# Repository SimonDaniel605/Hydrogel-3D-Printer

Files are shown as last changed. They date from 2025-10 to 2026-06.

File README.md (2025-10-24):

# Hydrogel-3D-Printer

This project aims at the development of a custom hydrogel 3D printer for tissue engineering and research applications for Stellenbosch University. This is a 4th year project for SU's BEng Mechatronics program.

This repository contains the PCB design files, firmware, and supporting documentation for the Hydrogel 3D Printer project.

Name: Simon Craig DANIEL

Student Number: 25848887

Supervisor: Mr. Wayne Swart

Company: Stellenbosch University

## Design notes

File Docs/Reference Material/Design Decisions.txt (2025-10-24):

Based on DESCRIPTION OF PREFERRED FITS (ANSI B4.2): The syrine plunger will use a clearance fit of H9/d10. Therefore the Syringe must have an ID of 20.000-20.052mm and the plunger should have an OD of 19.851-19.935mm. This yields a diametral clearance of 0.065-0.201mm. 

Groove width will be 3.3mm and its diameter will be 16mm (https://ceetak.com/o-ring-calculator/)

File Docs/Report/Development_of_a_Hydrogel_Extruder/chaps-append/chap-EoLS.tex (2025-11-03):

\chapter{Responsible Use of Resources and End-of-Life Strategy }
\section*{Responsible Use of Resources}
The hydrogel bioprinter was developed with the goal of using efficient materials and reusable components. The majority of the mechanical system consists of standard parts, including aluminium extrusions, TR8x8 lead screws, GT2 belts and pulleys, NEMA17 stepper motors, and linear bearings, which can all be reused in future student projects. 6 small PLA parts were 3D printed (4 feet and 2 limit switch mounts), resulting in minimal filament waste. The printer also includes several custom aluminium components (such as the syringe and bed plate) to ensure durability, most of which are made from aluminium plates to minimize machine waste.

The custom PCB was designed to maximise modularity, re-usability, and upgradability, by incorporating 5 stepper ports with breakout driver headers (StepStick form factor), 12 V switching ports, EEPROM storage, USB and SD card interface, and various breakout pins ensuring that the circuit board can be adapted across many different embedded systems applications. The experimental phase used store-bought agar powder as a hydrogel surrogate gel that is safe, biodegradable, inexpensive, and did not require a special disposal method.

\section*{End-of-Life Strategy}

At the end of the bioprinter's operational life, it can be disassembled into its mechanical and electronic components. The aluminium extrusions, motors, and other standard parts can be reused in future university projects or recycled through standard metal recycling facilities (along with the rest of the custom aluminium components). The PCB can be re-purposed to operate in other mechatronic systems or responsibly disposed of as electronic-waste and the PLA components can be recycled. The bioprinter’s modular design ensures that its components can be repaired, upgraded, or replaced, thereby extending the system's operational life and minimising environmental impact.

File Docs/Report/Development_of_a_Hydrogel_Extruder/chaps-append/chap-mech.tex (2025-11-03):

\chapter{Mechanical Drawings}

\begin{center}
  
  \captionof{figure}{Mechanical drawing of the exploded syringe assembly.}
  \label{fig:explode}
\end{center}

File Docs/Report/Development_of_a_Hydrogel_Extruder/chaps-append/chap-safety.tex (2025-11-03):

\chapter{Risk Analysis and Safety Procedures}
\section*{Safety Overview}
The mechanical and embedded system design, assembly and testing of the hydrogel 3D printer were performed at home, in a personal workspace, rather than in an official university laboratory or workshop. The project was conducted using a low-voltage electronic system and non-hazardous materials, and therefore presented minimal risks to both the user and equipment. Safety considerations, associated with the project, focused mainly on the mechanical, electrical, and thermal hazards associated with component assembly, soldering, and system handling.

The workspace was kept neat, tidy and ventilated to reduce the probability of tripping, remove solder fumes, and maintain easy access to equipment. Hazards such as the sharp edges of cut aluminium extrusions were eliminated by filing all edges after cutting. In cases where risks could not be completely eliminated, such as the presence of hot surfaces and nipping points, careful handling procedures were followed. This included keeping hands clear of the printer whenever in operation during the calibration stage and avoiding contact with heated components such as the nozzle and heat sinks until sufficient cooling time had elapsed after the printer was powered-down. To ensure the safe operation of the electronic system, protective measures were also implemented, such as limiting stepper driver current and verifying circuit connections with a multimeter before supplying power to the system.
\section*{Activity based Risk Assessment}
A risk assessment for the project is provided in Table~\ref{tab:risk}, which identifies the potential risks associated with each of project activity. The table also lists the corresponding steps to mitigate the likelihood and severity of each hazard to ensure personal safety (P) and equipment safety (E).
\begin{table}[H]
\centering
\caption{Risk assessment for the hydrogel 3D printer's development}
\label{tab:risk}
\begin{tabular}{|p{2.4cm}|p{3.3cm}|p{1cm}|p{6.0cm}|}
\hline
\textbf{Activity} & \textbf{Risk} & \textbf{Risk Type} & \textbf{Mitigating Steps} \\ \hline
Cutting aluminium & Cuts from sharp edges or saw blade & P & File all cut edges; clamp parts securely during cutting. \\ \hline
Assembling the printer & Thread stripping or cracking of 3D printed parts & E & Avoid over-tightening bolts. \\ \hline
Soldering & Burns and inhalation of fumes & P & Solder in a ventilated area; keep the iron in its stand when not in use. \\ \hline
PCB assembly & Short circuits & E & Verify polarity of components; test for continuity; avoid over-soldering joints. \\ \hline
Operating motors & Excessive current draw of drivers & E & Set current limits on stepper drivers. \\ \hline
Operating the printer & Pinch points between moving parts & P & Keep hands clear of moving parts during operation. \\ \hline
Hot surfaces & Burns from heated nozzle and heat sinks & P & Keep hands clear of heated parts during operation; allow adequate cooling time after power-down before handling. \\ \hline
Circuit handling & Static discharge & E & Disconnect power before handling PCB; ensure correct breakout driver orientation. \\ \hline
\end{tabular}
\end{table}

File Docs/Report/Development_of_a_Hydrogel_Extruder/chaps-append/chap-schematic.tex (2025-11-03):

\chapter{Embedded Hardware}

\noindent This appendix shows the complete embedded system hardware design, including the 3D model, copper layer layouts, and schematic pages for the hydrogel 3D printer control circuit.

\section{PCB Layout}
\begin{center}
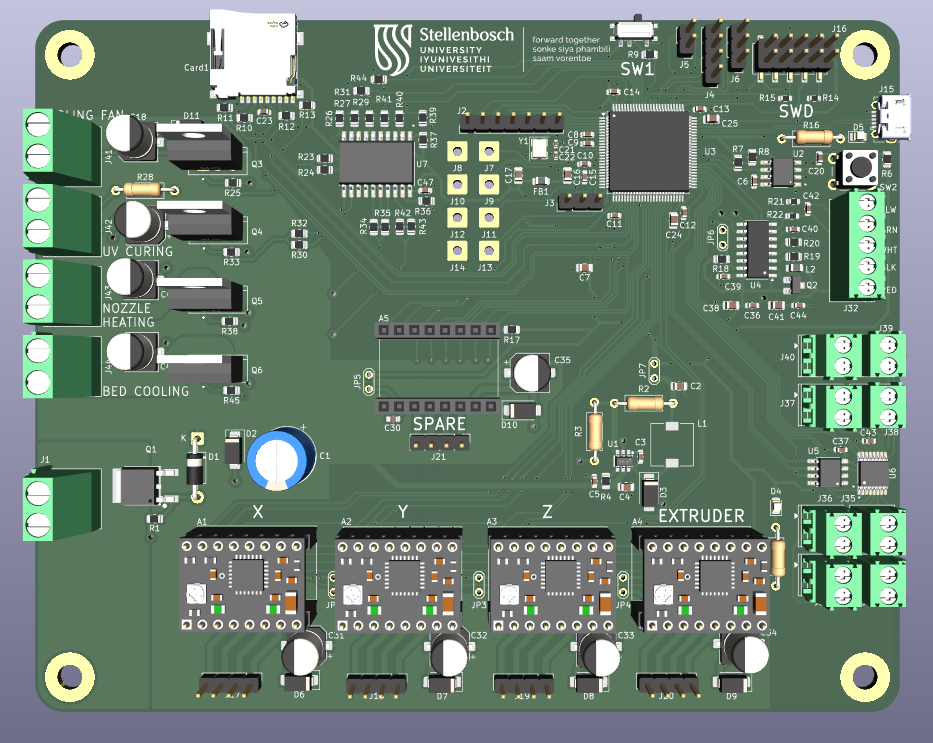
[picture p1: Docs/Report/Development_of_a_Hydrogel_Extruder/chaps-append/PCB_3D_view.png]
  
  \captionof{figure}{3D model of the assembled PCB illustrating overall component layout}
  \label{fig:pcb_3d_view}

  \vspace{1em}
  
  \captionof{figure}{Top layer layout showing signal routing and power traces.}
  \label{fig:pcb_top_layer}

  \vspace{1em}
  
  \captionof{figure}{Bottom layer layout showing ground planes, vias, and routing.}
  \label{fig:pcb_bottom_layer}
\end{center}

\section{Circuit Schematics}
\begin{center}
  
  \captionof{figure}{Schematic overview of the bioprinter control board.}
  \label{fig:pcb_overview}

  \vspace{1em}
  
  \captionof{figure}{Bioprinter power supply system schematic.}
  \label{fig:pcb_power}

  \vspace{1em}
  
  \captionof{figure}{Bioprinter stepper driver system schematic.}
  \label{fig:pcb_steppers}

  \vspace{1em}
  
  \captionof{figure}{Bioprinter sensor system schematic.}
  \label{fig:pcb_sensors}

  \vspace{1em}
  
  \captionof{figure}{Bioprinter control circuit schematic.}
  \label{fig:pcb_control}
\end{center}

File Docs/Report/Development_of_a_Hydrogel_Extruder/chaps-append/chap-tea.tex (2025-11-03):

\chapter{Techno-economic Analysis}
This section discusses the technical and economic aspects and impacts of the project. It covers time management, the project budget, technical impact, return on investment, and the project's potential for commercialisation.
\section{Planning and Time Management}
\begin{figure}[H]
    \centering
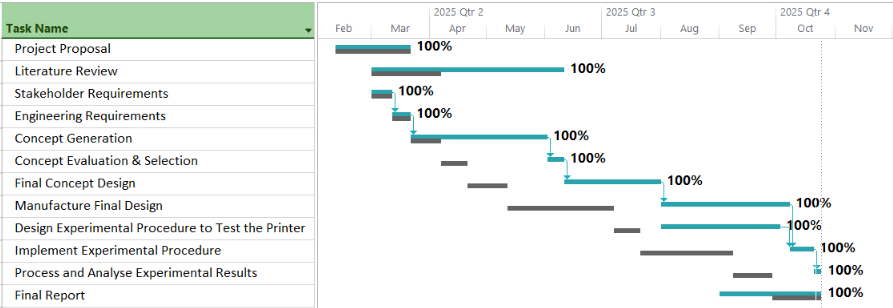
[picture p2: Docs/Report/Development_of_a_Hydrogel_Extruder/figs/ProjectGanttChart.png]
    
    \caption{Project Gantt Chart}
    \label{fig:gantt}
\end{figure}
The Gantt chart in Figure~\ref{fig:gantt} compares the predicted baseline duration (grey) of each project activity with the actual timeline (blue) in which the tasks were completed. It can be seen that the literature review extended over a significantly longer period than initially planned, due to the high workload from other modules during the first semester. A second major deviation occurred during the concept generation phase, which exceeded its planned duration because of an overly optimistic initial time estimate. The remaining project activities -- including completing the design process, manufacturing, assembling, and conducting the experimental work -- had to be completed within a shorter time frame to meet the final project deadline of 24~October~2025.

\section{Budget}
\begin{table}[H]
    \centering
    \caption{Estimated Project Budget}
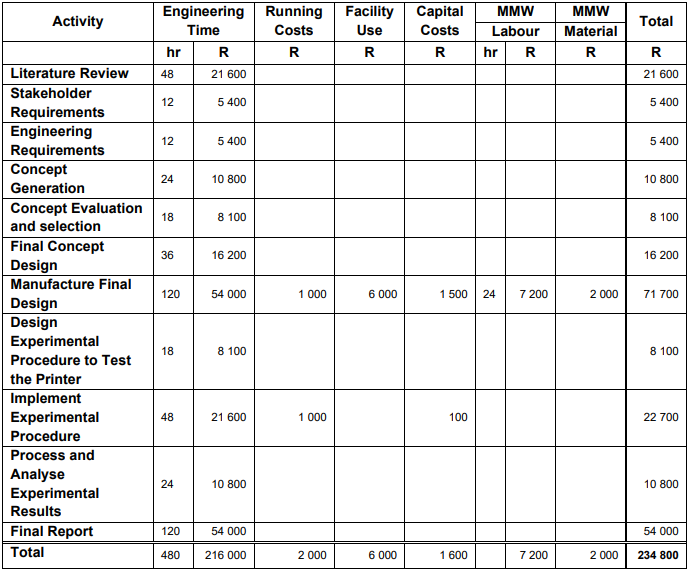
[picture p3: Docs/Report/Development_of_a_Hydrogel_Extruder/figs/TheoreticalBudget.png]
    
    \label{tab:theoreticalBud}
\end{table}
\begin{table}[H]
    \centering
    \caption{Actual Project Cost}
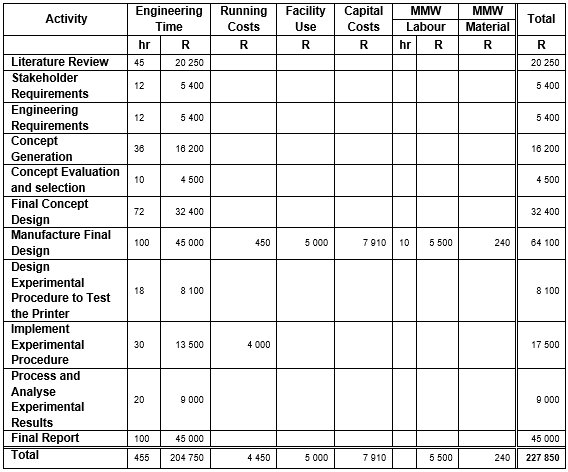
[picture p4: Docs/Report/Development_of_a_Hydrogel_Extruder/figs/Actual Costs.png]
    
    \label{tab:actualCost}
\end{table}
The predicted budget and estimated final costs are shown in Tables~\ref{tab:theoreticalBud} and~\ref{tab:actualCost}. The actual cost of R227 850 was slightly below the initially predicted budget of R234 800. The largest discrepancies between the planned and actual expenses occurred in the running, capital, and workshop cost categories. These differences occurred because the final design was completed after the proposed budget had been estimated. Therefore, many required components that needed to be purchased or manufactured were not yet identified. In addition, the running cost estimate did not accurately account for electricity consumption and unplanned consumables such as lubricant.

The cost of component procurement, whether manufactured by the university or externally sourced, is summarised in Table~\ref{tab:costs}. This table reflects the total cost of developing the complete prototype, excluding the engineering time required for the system design.
\begin{table}[H]
    \centering
    \caption{Prototype Costs}
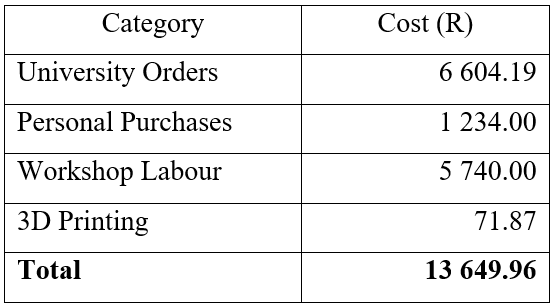
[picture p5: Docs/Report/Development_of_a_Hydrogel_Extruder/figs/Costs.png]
    
    \label{tab:costs}
\end{table}

\section{Technical Impact}
The development of the hydrogel 3D printer provides a meaningful technical contribution to biomedical and tissue engineering research. The project demonstrates that repeatable hydrogel extrusion can be achieved using a cost-effective bioprinting system. On a technical level, the functional prototype serves as a flexible research tool for studying flow behaviour of unknown hydrogels. Building on the first iteration of this project -- done in 2024 -- this prototype integrates embedded control, modular hardware, and tunable parameters. It has also lowered the cost barrier for local tissue engineering research and established a stronger foundation for continued bioprinter development within the university.
\section{Return on Investment}
The time and money that was invested into this project resulted in a functional research platform. In the short term, the bioprinter serves as a means of characterising different unknown gels. In the long term, the system offers a low-cost alternative to imported high-cost bioprinters. Further development of this project by future students can refine the prototype into a laboratory-grade bioprinter with temperature control and closed-loop pressure feedback. The project therefore provides a high return on investment through its affordability, adaptability, and potential use as a research tool.
\section{Potential for Commercialization}
The project outcome is a functional prototype of a hydrogel 3D printer that shows potential for commercialization as an affordable and modular bioprinter for research institutions. Current commercial bioprinters, like the BIO X series, are not accessible for many laboratories due to their high costs, creating a market opportunity for more affordable alternatives. The open-source firmware and modular design makes the system adaptable to a wide range of hydrogels. With further refinement in sterility and addition of closed-loop syringe temperature and pressure control, an enclosure design, and user interface, the prototype can be developed to serve as a low-cost bioprinter for creating cell-laden scaffolds and characterising hydrogels for universities and other research institutions.

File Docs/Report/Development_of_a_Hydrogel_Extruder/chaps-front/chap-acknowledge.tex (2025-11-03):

\chapter*{Acknowledgements}

I thank my Lord for sustaining me through this year and throughout my engineering degree, and for giving me the strength to complete my final-year skripsie project.
\vspace{0.5cm}

\noindent I am grateful to my supervisor, Mr. Swart, for his guidance throughout this project and for helping me broaden my range of engineering skills.
\vspace{0.5cm}

\noindent Lastly, I wish to thank my parents for their continuous support across my degree, and Stacey Sandy for her unwavering support and encouragement during my most academically challenging year.

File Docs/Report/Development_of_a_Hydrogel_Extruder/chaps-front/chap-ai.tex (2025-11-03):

\chapter*{AI Use Declaration}

{\setlength\labelwidth{1em}%
 \setlength\labelsep{5pt}%
 \setlength\itemindent{0pt}%
 \setlength\leftmargini{\labelwidth}%
 \setlength\topsep{0pt}%
 \setlength\partopsep{0pt}%
\begin{enumerate}
    \setlength\itemsep{\smallskipamount}%
    \setlength\parskip{0pt}%
    \small
    
    \item I am convinced and can support my claim that my assessment product is an indication of my own learning, knowledge, skills, and understanding.
    
    \item Where I have used AI tools for enhancing my own creation of ideas and words, I acknowledge that I have to declare it.
    
    \item Where I have used AI tools for generating new ideas, words, code, image-prompts for other AI Image-generating tools, or structure and even presentations (or other AI tools that can be used as assistants to the knowledge building and representing process), I have declared and documented the use of such tools and I am prepared to talk about the process I used and what it contributed to my learning and insights.
    
    \item I am aware that the lecturer can ask me to demonstrate my learning, for example through explaining the choices I made in terms of approach, content used, literature selected, conclusions drawn, etc. through an additional assessment like an oral (for example).
    
    \item I understand that if I am not able to agree to the above points, there is a chance that my academic behaviour will be deemed unethical and might lead to a disciplinary case being brought against me on the grounds of cheating or plagiarism and that the standard procedures for such behaviour will be followed.
    
    \item As per the Disciplinary Code of SU (par. 10.2.1 and 10.2.2), I understand that I take responsibility for the integrity of my work, which includes the obligation to ask for clarification from an academic member of staff if I am unsure of anything, and that I strictly adhered to all instructions received in the course of the academic assessment by relevant and authorized staff (whether the instruction is in oral or written format).
    
    \item I understand that when I am not able to document and declare my use of AI tools, this behaviour will be deemed as cheating in examinations and assessments (Disciplinary Code 1.1 c.) as I referred to “unauthorized notes, books, electronic devices or other reference material”.
\end{enumerate}}
\vspace{10mm}

\noindent
\begin{tabular}{@{}lllll@{}}
\tstrut Signature: & \sigfield[4cm]{figs/signature.png} &            &            \\
\tstrut Name:      & \makebox[5cm][l]{\shortstack[l]{Simon Craig Daniel \\ \dotfill}}
                   & Student no: & \makebox[3cm][l]{\shortstack[l]{25848887 \\ \dotfill}} \\
\tstrut Date:      & \makebox[4cm][l]{\shortstack[l]{24~October~2025     \\ \dotfill}} & & \\
\end{tabular}

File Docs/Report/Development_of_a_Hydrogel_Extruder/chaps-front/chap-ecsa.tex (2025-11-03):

\chapter*{ECSA self-assessment}

\renewcommand{\arraystretch}{1.5}
\begin{center}
\begin{longtable}{|m{\textwidth}|}
\hline

\textbf{GA 1. Problem solving} \\
\hline    
The project required problem solving to overcome multiple challenges in producing accurate and repeatable hydrogel prints. These included achieving controlled and stable extrusion of gels with complex non-Newtonian rheological properties, ensuring the system was adaptable to a range of bioinks, and providing a method to determine optimal printing parameters for different inks. Problem-solving ability is demonstrated in the mechanical, electronic, firmware, and experimental design aspects of the project. \\
\hline    

\textbf{GA 2. Application of scientific and engineering knowledge} \\
\hline    
The project required the integration of knowledge across mechanics, electronics, biology, and experimental design to develop a functional hydrogel printer. Mechanical analysis was used to calculate buckling loads in the syringe and to size actuators by determining the forces and speeds required for each stepper motor. Fluid mechanics principles, including Poiseuille’s law, were applied to estimate extrusion pressures and inform the syringe design. Circuit analysis and embedded systems knowledge were applied in designing and programming the custom PCB for control and sensing. Biological understanding of tissue engineering provided the performance requirements that shaped the system’s capabilities, while experimental design ensured validation of the printer's capabilities. \\
\hline    

\textbf{GA 3. Engineering Design} \\
\hline    
Engineering design was a major aspect of the project and was carried out across three primary phases: mechanical, embedded system, and experimental design. The mechanical design focused on developing the syringe-based extruder and gantry; the embedded system design centred on creating a custom PCB to control motion and sensing; and the experimental design established a methodology for determining the optimal printing parameters of a chosen bioink. Together these phases demonstrate a structured, multidisciplinary approach to achieving a functional bioprinter. \\
\hline    

\textbf{GA 5. Engineering methods, skills and tools, including Information Technology} \\
\hline    
The project required a wide range of engineering methods, skills and tools to design, build, and experimentally evaluate the 3D printer. Inventor Professional was used to create a 3D model of the mechanical bioprinter design. Analytical methods were applied to calculate mechanical loads, extrusion pressures, and motor requirements. Embedded hardware was designed using KiCad and the firmware was created through STM32CubeIDE. Experimental methods, supported by data processing in MATLAB, were applied to test the system and optimise printing parameters. \\
\hline    
    
\textbf{GA 6. Professional and technical communication} \\
\hline    
The project outcomes were communicated through an oral presentation and a detailed written report, supported by engineering drawings, schematics, and results. These demonstrated the ability to communicate information regarding technical work to engineering audiences. \\
\hline    

\textbf{GA 8. Individual, Team and Multidisciplinary Working} \\
\hline    
The project demonstrated independent execution while drawing on knowledge from multiple disciplines, including mechanics of materials, fluid mechanics, electronics, embedded software development, and biology. Collaboration with Stellenbosch University’s workshop artisans and the Physiology Department ensured the system was manufacturable and aligned with clear design objectives. \\
\hline    

\textbf{GA 9. Independent Learning Ability} \\
\hline    
Independent learning was demonstrated in several aspects of the project such as the literature review, which provided foundational knowledge in tissue engineering and hydrogel material science, as well as exposure to new approaches in mechanical design. New skills were gained in PCB design using KiCad, which enabled the development of the bioprinter's circuit board for sensing and control. \\
\hline    

\end{longtable}
\end{center}

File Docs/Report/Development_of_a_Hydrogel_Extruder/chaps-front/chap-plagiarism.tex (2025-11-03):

\chapter*{Plagiarism declaration}

I have read and understand the Stellenbosch University Policy on Plagiarism and the definitions of plagiarism and self-plagiarism contained in the Policy [Plagiarism: The use of the ideas or material of others without acknowledgement, or the re-use of one's own previously evaluated or published material without acknowledgement or indication thereof (self-plagiarism or text-\-re\-cyc\-ling)].

I also understand that direct translations are plagiarism, unless accompanied by an appropriate acknowledgement of the source. I also know that verbatim copy that has not been explicitly indicated as such, is plagiarism.

I know that plagiarism is a punishable offence and may be referred to the University's Central Disciplinary Committee (CDC) who has the authority to expel me for such an offence.

I know that plagiarism is harmful for the academic environment and that it has a negative impact on any profession.

Accordingly all quotations and contributions from any source whatsoever (including the internet) have been cited fully (acknowledged); further, all verbatim copies have been expressly indicated as such (e.g. through quotation marks) and the sources are cited fully.

I declare that, except where a source has been cited, the work contained in this assignment is my own work and that I have not previously (in its entirety or in part) submitted it for grading in this module/assignment or another module/assignment.
I declare that have not allowed, and will not allow, anyone to use my work (in paper, graphics, electronic, verbal or any other format) with the intention of passing it off as his/her own work.

I know that a mark of zero may be awarded to assignments with plagiarism and also that no opportunity be given to submit an improved assignment. 
\vspace{1.5cm}

\noindent
\begin{tabular}{@{}lllll@{}}
\tstrut Signature: & \sigfield[4cm]{figs/signature.png} &            &            \\
\tstrut Name:      & \makebox[5cm][l]{\shortstack[l]{Simon Craig Daniel \\ \dotfill}}
                   & Student no: & \makebox[3cm][l]{\shortstack[l]{25848887 \\ \dotfill}} \\
\tstrut Date:      & \makebox[4cm][l]{\shortstack[l]{24~October~2025 \\ \dotfill}} & & \\
\end{tabular}

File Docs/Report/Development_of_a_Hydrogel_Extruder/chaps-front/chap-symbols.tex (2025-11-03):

\chapter{List of symbols}
% Use stb-nomenclature + siunitx

\begin{Nomencl}[1cm]
\NomGroup{Constants}%-----------------------------------------------
    \item[$\pi = 3.1416...$]
    \item[$g = 9.81\; m\cdot s^2$]
    
\NomGroup{Variables}%-----------------------------------------------
    \item[$\mu$]       \UnitLine{Viscosity}{Pa\cdot s}
    \item[$Q$]         \UnitLine{Volumetric flow rate}{mm^3\cdot s^{-1}}
    \item[$v$]         \UnitLine{Extrusion rate}{mm\cdot s^{-1}}
    \item[$P$]         \UnitLine{Pressure}{Pa}
    \item[$N$]         \UnitLine{Force}{N}
    
\NomGroup{Subscripts}%----------------------------------------------
    \item[$\mathrm{atm}$] Atmospheric
    \item[$SF$]          Safety Factor

\end{Nomencl}

\begin{Nomencl}[1cm]
\NomGroup{Abreviations}%----------------------------------------------
    \item[SU] Stellenbosch Univerisity
    \item[GelMA] Gelatin Methacrylate
    \item[PEGDA] Polyethylene Glycol Diacrylate
    \item[PVA] Polyvinyl Alcohol
    \item[EM] Extracellular Matrix
    \item[UV] Ultraviolet
    \item[CAD] Computer-Aided Design    
    \item[PCB] Printed Circuit Board
    \item[PSU] Power Supply Unit
    \item[SWD] Serial Wire Debug
    \item[ISR] Interrupt Service Routine
\end{Nomencl}

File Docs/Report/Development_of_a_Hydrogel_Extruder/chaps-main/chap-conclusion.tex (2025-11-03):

\chapter{Conclusions}
\section{Future Work}
While the printer achieved its primary goals of producing repeatable, stable extrusion of hydrogel to create 3D scaffolds, certain functional requirements were not met due to the project's broad scope and the time constraints imposed by hardware setbacks, leaving them for future implementation.

These outstanding functions include temperature and pressure sensing with feedback control, even though the electronic system was designed to support them. Implementing pressure sensing for closed-loop PID control to achieve highly accurate extrusion rates remains a key feature for future iterations of the project. Similarly, temperature sensing for both the bed and nozzle is required to be implemented in the future to enable closed loop thermal feedback for bed and nozzle thermal regulation, ensuring consistent printing conditions and improved repeatability.

\section{Final Conclusions}
The bioprinter developed in this project successfully demonstrated accurate and repeatable extrusion capable of producing multi-layered scaffolds through a low-cost and modular design. The integration of the mechanical, electronic, and firmware subsystms provided the printer with the ability to control motion and flow parameters, enabling consist and adjustable printing outcomes after calibration with the surrogate agar gel.

Despite delays and unimplemented control loops, the printing system achieved its primary objectives by serving as a calibration tool for characterising unknown bioinks and using them to create scaffolds, thereby validating the experimental design.

Overall, the project was successful and demonstrated the potential for developing low-cost bioprinter alternatives that can serve as research tools in the biomedical field. It provides a strong foundation for future students to improve the design, complete the outstanding feedback control, and expand the calibration procedure to further improve print quality and capability. Ultimately, this research lays the groundwork for Stellenbosch University to develop a fully automated, high-quality bioprinter that can be integrated into the Physiology Department's research environment.

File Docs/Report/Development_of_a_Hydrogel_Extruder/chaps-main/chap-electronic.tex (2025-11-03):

\chapter{Embedded System Design}
This chapter details the design and implementation of the embedded control system for the hydrogel bioprinter. The embedded system is responsible for coordinating the mechatronic system’s core functions, including stepper movement, memory management, bed and nozzle temperature control, and UV curing. The electronic hardware design takes the form of a custom PCB featuring an STM32F407VGT6 microcontroller, which executes the developed firmware to allow the printer to function. While more affordable alternatives exist, the STM32F407VGT6 was selected based on prior experience, thereby reducing development time and the learning curve.

The embedded system was designed to meet the following requirements, developed for the electronic design in order to allow the whole system to meet the stakeholder requirements from chapter 3:

\begin{itemize}
    \item The system must safely supply regulated 3.3 V to the logic subsystems from a 12 V DC power supply that plugs into a standard wall socket.
    \item The system must be able to drive up to five stepper motors through A4988 driver breakout modules.
    \item The system must be able to receive real-time sensor data, including extrusion force from a load cell and temperature readings from thermocouples.
    \item The device must implement switching control for a heater cartridge, Peltier module, UV curing light, and cooling fan.
    \item The system is required to receive print task via a microSD card.
    \item The printer must implement feedback control loops for extrusion pressure and temperature regulation.
    \item The system must provide headers for unused controller pins to support future upgrades.
\end{itemize}

The final assembled hydrogel bioprinter, including the implemented embedded system, is shown below in Figure~\ref{fig:FinalPrinter}:
\begin{figure}[H]
    \centering
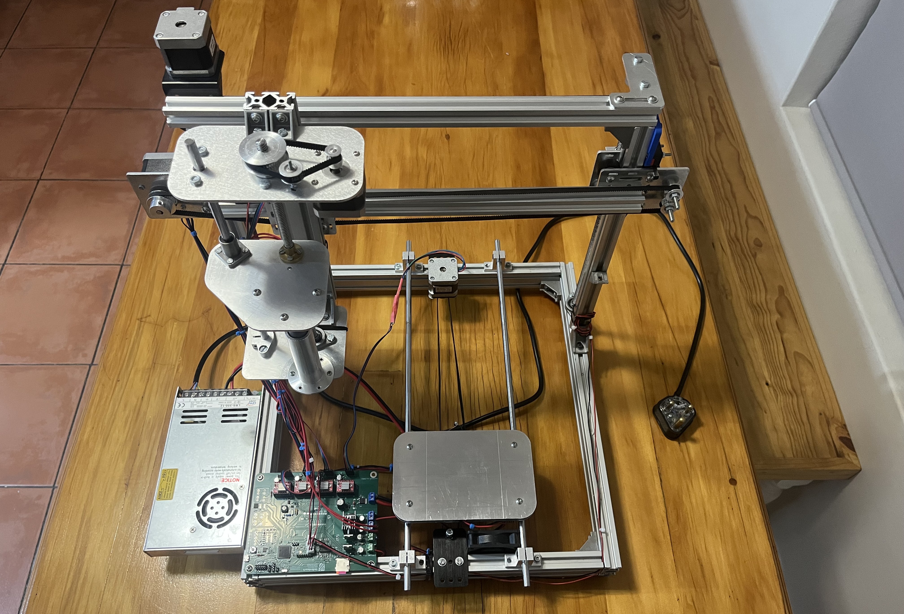
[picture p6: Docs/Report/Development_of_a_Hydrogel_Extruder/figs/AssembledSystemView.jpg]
    
    \caption{The Final Assembled Hydrogel Bioprinter}
    \label{fig:FinalPrinter}
\end{figure}

\section{System Description}
The embedded system as a whole enables the printer's automated operation. It is powered by a 12 V PSU that directly supplies power to the stepper drivers, Peltier module, UV curing light, heater cartridge, and cooling fan. The 12 V is also converted into a regulated 3.3 V source via a buck converter to power the logic circuits. The STM32 controller reads print instructions from a microSD card so that it can then control the stepper motors (through drivers) using an ISR. During stepper operation, system information is transmitted to a laptop via a USB connection for external monitoring. External peripherals (Peltier, heater cartridge, cooling fan, and curing light) are connected to the 12 V source and switched between their ON and OFF states using N-channel power MOSFETs.

This description of the system is visually represented in the block diagram below in Figure~\ref{systemblockdiagram}. The black arrows represent the logic flow, the red arrows show the 12 V power distribution, and the green arrow shows how the 3.3 V power source is distributed.
    
\begin{figure}[H]
\centering
\begin{tikzpicture}[
  voltagecircle/.style = {circle, draw=black, thick, minimum size=1.2cm, align=center},
  block/.style = {rectangle, draw=black, thick, minimum width=3.5cm, minimum height=1cm, align=center},
  mcu/.style = {rectangle, rounded corners=5pt, draw=black, thick, minimum width=1cm, minimum height=3cm, align=center, fill=white},
  lp/.style = {rectangle, rounded corners=5pt, draw=black, thick, minimum width=1cm, minimum height=1.5cm, align=center, fill=white},
  io/.style = {rectangle, rounded corners=5pt, draw=black, thick, minimum width=2.5cm, minimum height=1cm, align=center},
  arrow/.style = {thick, -{Latex[scale=1.2]}},
  arrow2/.style = {thick, -{Latex[scale=1.2]}, color=red},
  arrow3/.style = {thick, -{Latex[scale=1.2]}, color=green}
]

% Power supply chain
\node[voltagecircle] (src) at (0.45, 8.5) {12 V\\Source};
\node[block] (reg3v3) at (5, 8.5) {3.3 V Regulator};
\node[mcu] (mcu) at (5, 4) {STM32F407\\MCU};
% Right
\node[io] (switch) at (9.2, 7.5) {Limit Switches};
\node[io] (temp) at (9.8, 6) {Temperature Sensors};
\node[io] (load) at (10, 4.5) {Extrusion Force Sensor};
\node[io] (eeprom) at (9.1, 3) {EEPROM};
\node[io] (sdcard) at (9.3, 1.5) {microSD Card};
% Left
\node[io] (step) at (0.45, 4.5) {Stepper Drivers};
\node[io] (fet) at (0, 3) {Switching MOSFETs};
% Bottom
\node[io] (usb) at (5, 1.5) {USB connection};
\node[lp] (laptop) at (0, 1.5) {Laptop};
% 12V Power flow arrows
\draw[arrow2] (src.east) -- (reg3v3.west);
\draw[arrow2] (src.south) -- (step.north);
\draw[arrow2] (0.45, 5.5) -- (-1.5, 5.5) -- (-1.5, 3.5);
% 3v3 Power flow arrows
\draw[arrow3] (reg3v3.east) -- (13,8.5) -- (13,1.5) -- (sdcard.east);
\draw[arrow3] (13,3) -- (eeprom.east);
\draw[arrow3] (13,4.5) -- (load.east);
\draw[arrow3] (13,6) -- (temp.east);
\draw[arrow3] (reg3v3.south) -- (mcu.north);
\draw[arrow3] (5,6) -- (1.5,6) -- (1.5,5);
% Logic flow arrows
\draw[arrow] (mcu.south) -- (usb.north);
\draw[arrow] (usb.west) -- (laptop.east);
\draw[arrow] (switch.west) -- (5.7,7.5) -- (5.7, 5.49);
\draw[arrow] (temp.west) -- (6.7,6) -- (6.7, 5) -- (6.2, 5);
\draw[arrow] (load.west) -- (6.2,4.5);
\draw[arrow] (eeprom.west) -- (6.25, 3);
\draw[arrow] (6.25, 3) -- (eeprom.west);
\draw[arrow] (sdcard.west) -- (6.9,1.5) -- (6.9, 2.7) -- (6.2, 2.7);
\draw[arrow] (3.77, 4.5) -- (step.east);
\draw[arrow] (3.77, 3) -- (fet.east);

\end{tikzpicture}
\caption{System Block Diagram of the Bioprinter's Embedded System}
\label{systemblockdiagram}
\end{figure}

\section{Hardware Design and Implementation}
The hardware design, as previously stated, took place in the form of a custom PCB. The PCB was designed using KiCad and manufactured by JLCPCB. The electronic system can be separated into various subsystems, including the power supply, stepper drivers, limit switches, memory handling circuit, load cell sensing circuit, temperature reading circuit, and the N-channel MOSFET switching circuit. The timing of each subsystem is coordinated by a high-speed crystal oscillator. A schematic overview of the PCB is shown in Figure~\ref{fig:pcb_overview} in Appendix C.

\subsection{Power Supply}
The power supply subsystem, shown in Figure~\ref{fig:pcb_power}, incorporates both circuit protection and voltage conversion through a buck converter. The printer is powered by a 350 W LRS PSU, which allows direct connection to a standard wall socket and converts the municipal 230 $V_{\text{RMS}}$ supply into a regulated 12 V DC output. This output is delivered to the PCB via screw terminals. 

In the event of incorrect wiring, the system makes use of reverse polarity protection using a high-side P-channel MOSFET. This ensures that, if the ground and 12 V connection are swapped, the source output is 0 V instead of -12 V. This method was chosen over a simple series diode to eliminate forward voltage drop and preserve the full 12 V for the stepper drivers and switching peripherals. 

The entire circuit board also uses bulk and decoupling capacitors to filter out a wide range of frequencies to produce stable voltage levels for both 12 V and 3.3 V components. The 12 V source also makes use of TVS diodes (SMAJ16A) positioned near inductive loads, such as the buck converter, stepper drivers, and cooling fan port, to suppress transient voltage spikes.

This subsystem also has the role of producing a stable 3.3 V source for the logic circuitry. To do this, the PCB uses an AP3211 buck converter, following the typical \SI{12}{V} to \SI{3.3}{V} application circuit by \cite{AP3211}.
\subsection{Power Debug LEDs}
The electronic hardware incorporates debug LEDs to show the presence of specific voltage levels. A green LED ($V_f \approx$\SI{2}{V}) is connected to the buck converter's 3.3 V output to confirm that the system is connected to power and that the input voltage is successfully converted to 3.3 V. A second debug LED, a blue LED ($V_f \approx$\SI{3}{V}), is connected to the USB port's 5 V pin to show when the board is connected to a laptop via USB. Both LEDs require current limiting resistors, which were calculated to limit the current to 10 mA as follows:
\begin{align*}
R_{3.3\text{V}} = \frac{3.3\ \text{V} - 2.0\ \text{V}}{10\ \text{mA}}
= 130\ \Omega
\,\,\,\,\,\,\,\,\,\,\, \text{ and } \,\,\,\,\,\,\,\,\,\,\,
R_{5\text{V}} = \frac{5.0\ \text{V} - 3.0\ \text{V}}{10\ \text{mA}}
= 200\ \Omega.
\end{align*}
For an added safety margin, \SI{220}{\ohm} resistors were used for both LEDs.

\subsection{Stepper Driver Interface}
To interface with the stepper motors, the PCB employs five A4988 driver modules, as shown in Figure~\ref{fig:pcb_steppers}. Three drivers control the motors of the 3-axis gantry, one drives the extruder stepper, and one spare driver is included to allow future upgrades, such as the addition of a second extruder. The A4988 drivers come in the form of Pololu breakout modules that plug into female headers on the PCB (visible in the 3D model in Appendix B.9). The advantage of using socketed breakout drivers is that they can be easily replaced in the event of damage. The headers follow the StepStick form factor which means the A4988 drivers can be replaced with more advanced drivers such as the TMC2209. While each driver requires a dedicated GPIO pin for its STEP and DIR inputs, to conserve controller pins, the $\overline{En}$, $\overline{SLEEP}$, $\overline{RESET}$, and the microstepping setting pins (M0, M1, and M2) are shared across all five drivers.

To limit the current, the potentiometer on each stepper driver needs to be adjusted to reach a desired reference voltage which can be obtained using the following formula: 
\[
I_{\text{limit}} \;=\; \frac{V_{\text{ref}}}{8 R_{\text{sense}}}
\qquad\Longleftrightarrow\qquad
V_{\text{ref}} \;=\; 8R_{\text{sense}}\cdot I_{\text{limit}}.
\]

By looking at the drivers and checking the stepper motor specifications, it can be concluded that:
\begin{itemize}
    \item \(R_{\text{sense}} = 0.10~\Omega\)
    \item \(I_{\text{limit}} = 1.0~\text{A}\)
\end{itemize}

\[V_{\text{ref}} \;=\; 8\cdot 0.10\cdot 1.0=0.8\text{ A.}\]

\subsection{Limit Switches}
Figure~\ref{fig:pcb_overview} shows that the circuit board provides four limit switch connection points. Only three are utilised to allow for the homing of each gantry axis. The COM pin of each limit switch is connected to ground and the NO pin is connected to a dedicated GPIO input pin (PC0-PC2) that is pulled high so that when each axis reaches the end of its range of motion, the switch gets triggered and is pulled low.
\subsection{Memory and Connectivity Interfaces}
The board employs various means of handling memory and connecting with external devices, both for reading and transmitting data as well as for programming and debugging. This functions are achieved through the inclusion of an EEPROM, a microSD port, a USB port, and an SWD interface (Figure~\ref{fig:pcb_overview}).

The controller is connected to an M24C64 EEPROM, which provides a means of storing non-volatile information via an \(I^2C\) connection, ensuring that data can be retained even after the printer’s power source is disconnected. In addition to this, the circuit board incorporates a microSD card port for reading print task files through the MCU’s SPI1 channel. A USB port is also included, allowing the board to connect to a laptop and transmit live data—such as temperature and extrusion force readings for external monitoring and analysis. Because the USB interface requires a highly accurate clock speed (48 MHz) for reliable data transmission, the PCB includes a 16 MHz external crystal oscillator to provide a precise reference for the phase-locked loop \citep{ST_STM32F405F407_datasheet}.

For programming and debugging, the board includes a 2×5 male header array. Each pin in the header is connected to the relevant system points, including the 3.3 V supply, ground, and the required STM32 pins (SWDIO, SWCLK, SWO, and NRST). During development, these SWD pins were connected to the corresponding pins of an STM32F407G-DISC1 development board to enable programming and debugging via its integrated ST-Link interface.

To improve modularity and support future upgrades, the board includes expansion headers that connect to unused MCU pins (Figure~\ref{fig:pcb_power}). These pins connect to spare GPIO, ADC, USART, \(I^2C\), and SPI channels, enabling potential additions such as external displays.

\subsection{Load Cell Circuit}
Figure~\ref{fig:pcb_sensors} shows the circuits sensor system which includes extrusion force sensing using a load cell amplifier. The amplifier circuit design was based on the SparkFun open-source HX711 load cell amplifier breakout module \citep{SparkFunHX711}. This is powered by the board's 3.3 V supply and connected to two controller GPIO pins (a clock pin and an input pin). The board has four relevant screw terminal connection points for an external load cell (RED, BLACK, WHITE, and GREEN).

The 50 kg load cell used to measure the extrusion force is configured as a half Wheatstone bridge (containing two \SI{1}{\kilo\ohm} resistors). To form a complete Wheatstone bridge, two additional \SI{1}{\kilo\ohm} resistors are required, as shown in the full load cell–to–PCB set-up in Figure~\ref{fig:loadcell}.
\begin{figure}[H]
\centering
\begin{tikzpicture}[
  block/.style = {rectangle, draw=black, thick, minimum width=1.2cm, minimum height=0.8cm, align=center},
  lc/.style = {rectangle, rounded corners=5pt, draw=black, thick, minimum width=2.5cm, minimum height=3cm, align=left},
  pcb/.style = {
  rectangle, rounded corners=5pt, draw=black, thick,
  text width=4cm,            % content width
  inner xsep=8pt, inner ysep=20pt,
  align=left
  },
  arrow/.style = {thick, -{Latex[scale=1.2]}}
]

% Power supply chain
\node[lc] (loadcell) at (0, 0) {50 kg\\ Load Cell};
\node[pcb] (board) at (10,0.3) {RED \\[10pt] BLACK \\[10pt] WHITE \\[10pt] GREEN};
\node[block] (res1) at (4, 1) {\SI{1}{\kilo\ohm}};
\node[block] (res2) at (4, 0) {\SI{1}{\kilo\ohm}};
% connections
\draw (1.25,-1) -- (7.73,-1);
\draw (1.25, 0) -- (3.4,0);
\draw (1.25, 1) -- (3.4,1);
\draw (4.6, 1) -- (5,1) -- (5,-0.1) -- (7.73,-0.1);
\draw (4.6, 0) -- (5,0);
\draw (2.7,0) -- (2.7,0.75) 
      arc[start angle=-90,end angle=90,radius=0.25cm] -- (2.7,1.7) -- (5.3,1.7) -- (5.3,0.7) -- (7.73,0.7);
\draw (2,1) -- (2,2) -- (5.6,2) -- (5.6,1.6) -- (7.73,1.6);

\node at (7.2,1.8) {E+};
\node at (7.1,0.9) {E-};
\node at (7.1,0.1) {A-};
\node at (7.2,-0.8) {A+};
\end{tikzpicture}
\caption{Load Cell Setup}
\label{fig:loadcell}
\end{figure}

\subsection{Thermocouple Circuit}
The temperature sensing circuit is shown in Figure~\ref{fig:pcb_sensors}. This uses a MAX6675 K-type thermocouple, which is connected to the STM32's SPI2 pins (PB12-PB14). The amplifier receives the analogue thermocouple input, converts the signal into a digital value, and outputs this to the controller via the Serial Peripheral Interface. 

To allow the controller to read multiple thermocouples using a single amplifier, an analogue multiplexer (TMUX1208) is used. The MUX cycles through eight two-pin thermocouple screw terminals, where the T+ line connects to the amplifier input and the T– line is tied to ground. Channel selection is controlled by the MUX’s enable pin (EN) and three select pins (A0, A1, A2). The binary combination of these pins determines which of the eight thermocouple channels is connected to the amplifier input at a given time.

\subsection{FET Switching Circuit}
Figure~\ref{fig:pcb_control} shows the control circuit responsible for switching the system's various 12 V peripherals. These 12 V peripherals (each connected via two-pin screw terminals), include a Peltier cooling module, an E3D heater cartridge, a cooling fan, and a UV curing light. For safety reasons and due to the use of a non-curable surrogate gel in the experimental procedure (described in Chapter 5), a blue led was used in place of the UV light to demonstrate functionality. 

The peripherals are switched using N-Channel power MOSFETs (IRLZ44N), which are capable of handling high currents required by components such as the Peltier module (maximum current 7 A). The transistors are configured as low-side switches, with their source terminals tied to ground, drains connected to the negative side of the loads, and gates driven by STM32 GPIO outputs. If fully implemented, a UV light would be kept in a fixed position and flood the print bed with an adjustable intensity, which would be set by a duty cycle read from the microSD card during print commands.

A potential issue with this arrangement is that the transistor gates act as capacitive loads. When GPIO outputs transitions from high to low, the stored charge from the gate capacitance discharges into the MCU pin as a temporary transient discharge current. Since each GPIO pin is only rated for 25 mA \citep{ST_STM32F405F407_datasheet}, this risks damaging the controller. To mitigate this, small series resistors are placed at each gate to limit the initial discharge current.  In addition, an octal bus transceiver (SN74HC245DWR) is used as a protective buffer stage between the MCU and the MOSFET gates. This configuration not only shields the microcontroller from harmful transient currents but also improves signal integrity when driving multiple high-capacitance gates.

\subsection{PCB Design}
The embedded hardware was implemented on a custom PCB designed in KiCad and fabricated by JLCPCB. Its design required a number of engineering decisions regarding trace widths, layer count, and overall routing strategy.

The PCB is a two-layer board, with the bottom copper layer serving primarily as a ground plane and the top layer carrying power and signal routes. The complete board layout is shown in Figures~\ref{fig:pcb_3d_view} to~\ref{fig:pcb_bottom_layer}. In areas supplying the 12 V peripherals, such as the switching MOSFETs and stepper drivers, the top copper includes solid planes to provide sufficient current capacity while minimizing temperature rise.

Signal routing on the top layer generally uses 0.3 mm traces, while 3.3 V power lines were widened to 0.5 mm. The 0.5~mm trace width is justified through the empirically derived IPC-2221 current-temperature relationship, to estimate a minimum width (W) of a 1~oz/$ft^2$ thick copper trace to conduct the maximum buck-converter output current of 1.5~A with a $5~^\circ$C temperature rise:
\[
W = \frac{1}{t_{\text{cu}}}\left(\frac{I}{k(\Delta T)^{0.44}}\right)^{\frac{1}{0.725}} = \frac{1}{1.378}\left(\frac{1.5}{0.048(5)^{0.44}}\right)^{\frac{1}{0.725}} = 16.9~\text{mil} = 0.43~\text{mm}.
\]

Communication traces connecting the SD card, EEPROM, USB interface, MAX6675 thermocouple amplifier, and HX711 load cell amplifier to the STM32 microcontroller were deliberately kept short and closely routed to the MCU, with spacing between traces maximised (as far as reasonably possible) to preserve signal integrity. Similar care was taken around the buck converter circuitry to minimize interference arising from its high-frequency operation.

\section{Software Design and Implementation}
The firmware governs the 3D printer's operation. After initialising its peripherals, the system homes the gantry to its reference position and zeros the coordinate axes. It then enters an interrupt-driven routine that handles all stepper motion while the main loop cycles through system tasks such as SD card reading, USB transmission, and MOSFET duty cycle updates. The system's general software flow is visually represented in Figure~\ref{softwareflowdiagram}.

\begin{figure}[H]
\centering
\begin{tikzpicture}[
  circ/.style = {circle, draw=black, thick, minimum size=1.2cm, align=center},
  block/.style = {rectangle, draw=black, thick, minimum width=3.5cm, minimum height=1cm, align=center},
  io/.style = {rectangle, rounded corners=5pt, draw=black, thick, minimum width=2.5cm, minimum height=1cm, align=center},
  arrow/.style = {thick, -{Latex[scale=1.2]}}
]

\node[circ] (power) at (11, 5) {Power\\On};
\node[io] (sysInit) at (7.5, 5) {Initialize\\System};
\node[io] (home) at (3.5, 5) {Home};
\node[io] (zero) at (0, 5) {Zero\\Coordinates};

\node[io] (isr) at (3, 3.4) {Interrupt Service Routine};
\node[io] (step) at (8, 3.4) {Move Steppers};

\node[io] (queue) at (3, 1.7) {Add Task To\\ISR Queue};

\node[circ] (while) at (0, 0) {While\\Loop};
\node[io] (sd) at (3, 0) {Read\\SD Card};
\node[io] (fet) at (6, 0) {Update\\MOSFETs};
\node[io] (usb) at (9, 0) {USB\\Transmit};
\node[circ] (end) at (11.7, 0) {End of\\Loop};

% Logic flow arrows
\draw[arrow] (power.west) -- (sysInit.east);
\draw[arrow] (sysInit.west) -- (home.east);
\draw[arrow] (home.west) -- (zero.east);
\draw[arrow] (zero.south) -- (while.north);
\draw[arrow] (while.east) -- (sd.west);
\draw[arrow] (sd.east) -- (fet.west);
\draw[arrow] (fet.east) -- (usb.west);
\draw[arrow] (usb.east) -- (end.west);

\draw[arrow] (isr.east) -- (step.west);
\draw[arrow] (0, 3.4) -- (isr.west);

\draw[arrow] (sd.north) -- (queue.south);
\draw[arrow] (queue.north) -- (isr.south);
\end{tikzpicture}
\caption{Bioprinter's Generalised Software Flow Diagram}
\label{softwareflowdiagram}
\end{figure}

\subsection{Homing}
Upon startup, after all system peripherals have been initialised, the printer performs a homing sequence in which the gantry moves each of its three axes towards known reference positions (0, 0, 0). This procedure establishes the origin of the its coordinate system, ensuring that its absolute extruder position for a given coordinate remains consistent between power cycles.

The A4988 drivers are enabled (EN low, RESET and SLEEP high) and configured for 1/16 microstepping (M0,M1, and M2 high). Each driver's DIR pin is set so that each axis moves towards the corresponding limit switch. Each normally-open limit switch is connected to a dedicated GPIO input pin that is pulled high internally. When the limit switch closes, the input pin is connected to ground and goes low.

Step timing is handled by TIM5, which runs at 1~MHz (PSC = 83), giving a 1 µs counter tick. Each step pulse is held high for 5 µs and then low for an axis-specific duration so that each axis moves at approximately 16 mm/s. During homing, only one axis moves at a time until its limit switch GPIO input is no longer high, at which point that axis stops and the next axis begins. The axes are homed in the order of Z, Y, and lastly X.

\subsection{Stepper Logic}
After the gantry is homed, the printer's motion system is scheduled through an interrupt service routine (ISR). The advantage of timing the stepper movements with scheduled interrupts, rather than triggering each step from within the program’s \texttt{while(1)} loop, is that step pulses are consistently generated on time and remain unaffected by lower-priority tasks that could introduce delays. Although the firmware may not currently be performing computationally intensive operations that make this approach strictly necessary, it provides future-proofing by ensuring reliable motion control even as more time-demanding features (G-code parsing) are added.

Once the system is homed, the enable pin is set low, and the sleep and reset pins are set high as instructed by \cite{Allegro_A4988}. The microstep selection pins are all driven high to configure the driver for 1/16 microstepping mode, ensuring maximum positional accuracy for the belt-driven axes. The DIR pins for each driver are pre-defined in the code as high or low to define each axis' positive direction. Before the ISR starts executing the commands from the SD card, the stepper coordinates are set to zero with the command \texttt{Stepper\_ResetPosition(x0, y0, z0, e0)}.

\begin{figure}[H]
\centering
\begin{tikzpicture}[
  circ/.style = {circle, draw=black, thick, minimum size=1.2cm, align=center},
  block/.style = {rectangle, draw=black, thick, minimum width=3.5cm, minimum height=1cm, align=center},
  io/.style = {rectangle, rounded corners=5pt, draw=black, thick, minimum width=2.5cm, minimum height=1cm, align=center},
  arrow/.style = {thick, -{Latex[scale=1.2]}}
]
\node[circ] (init) at (11.5, 6.5) {Start ISR\\Segment};
\node[io] (calc) at (8.25, 6.5) {Calculate \\$N_x\,\text{and}\,N_\text{max}$};
\node[io] (reset) at (4.2, 6.5) {Reset accumulators\\($i=0\,\text{and}\,e_x=0$)};
\node[io] (dir) at (0, 6.5) {Set $\text{DIR}_x$};

\node[io] (queue) at (3, 5) {Start the next ISR\\segment in the queue};
\node (true1) at (2.2,4) {TRUE};
\node[circ] (interrupt) at (0, 3) {Interrupt\\Triggered};
\node[io] (comp1) at (3, 3) {$i \ge N_{\max}$};
\node (false1) at (5.1,3.3) {FALSE};

\node[io] (comp2) at (11, 3) {$e_x \ge N_{\max}$};
\node[io] (step) at (11, 1) {Generate\\step pulse};
\node[io] (sub) at (7, 1) {$e_x \leftarrow e_x - N_{\max}$};
\node[io] (wait) at (3, 0) {Wait for\\next interrupt};
\node (true2) at (10.3,2.2) {TRUE};
\node (false2) at (10.3,-0.3) {FALSE};
\node[io] (accum) at (7.5,3)
  {$\begin{aligned}
      e_x &\leftarrow e_x + N_x\\
      i   &\leftarrow i + 1
    \end{aligned}$};
% Logic flow arrows
\draw[arrow] (init.west) -- (calc.east);
\draw[arrow] (calc.west) -- (reset.east);
\draw[arrow] (reset.west) -- (dir.east);
\draw[arrow] (dir.south) -- (interrupt.north);
\draw[arrow] (interrupt.east) -- (comp1.west);
\draw[arrow] (comp1.north) -- (queue.south);
\draw[arrow] (comp1.east) -- (accum.west);
\draw[arrow] (accum.east) -- (comp2.west);
\draw[arrow] (comp2.south) -- (step.north);
\draw[arrow] (step.west) -- (sub.east);
\draw[arrow] (sub.west) -- (3,1) -- (wait.north);
\draw[arrow] (wait.west) -- (0,0) -- (interrupt.south);
\draw[arrow] (comp2.east) -- (12.5,3) -- (12.5,0) -- (wait.east);

\end{tikzpicture}
\caption{Software Diagram of an ISR Segment on the X-axis}
\label{isrdiagram}
\end{figure}

The ISR, driven by TIM1, implements motion commands executed from a circular queue. The commands use the format of x position, y position, z position, speed, extrusion rate, and a boolean input that determines whether the command is implemented according to a relative (1) or absolute (0) coordinate system. From this, the ISR operates with the following steps (shown in Figure~\ref{isrdiagram}):
\begin{itemize}
    \item The relative distance each axis must move is calculated (i.e. $\Delta x=x_{target}-x_{current}$).
    
    \item Using the steps per millimeter for each stepper, the required number of steps is determined (i.e. $N_x=|\Delta x \times \text{STEPS\_PER\_MM}| $).

    \item The direction level (DIR) is determined for each driver by considering the sign of each axis' position change and the positive direction level defined in the code.

    \item To determine the total execution time of each command, the travel length is calculated ($L=\sqrt{\Delta x^2+\Delta y^2+\Delta z^2}$), and the total time is then obtained by dividing this length by the gantry speed ($T=\frac{L}{v}$).

    \item To ensure that all axes arrive simultaneously, the maximum step count is calculated as $N_{max}=\text{max}(N_x,N_y,N_z,N_e)$.

    \item From this, the ISR runs at a frequency of $f_{\text{step}}=\frac{N_{\text{max}}}{T}$, and the interrupt period is the reciprocal.

    \item At each interrupt period, each axis increments its own Bresenham accumulator to determine whether a pulse must be generated for any of the drivers. For example, the x axis accumulator, $e_x$, increments by $N_x$ during each interrupt, but a step pulse is only generated for the x axis once $e_x\ge N_\text{max}$, in which case the accumulator will also be reduced by $N_\text{max}$.
\end{itemize}

\subsection{USB Communication}
The STM32 controller uses a USB Full-Speed CDC virtual COM port on PA11 and PA12 using the STM32 USB Device library. Upon startup, the USB system is initialised and a 1 Hz task transmits a message to communicate system information (such as temperature) via \texttt{CDC\_Transmit\_FS()}. The transmission is sent in the following format:
\begin{quote}\ttfamily
setNozTemp=30.00C, NozTemp=26.12C, Load=5.71 kg \textbackslash n
\end{quote}
A laptop can connect to the PCB via a USB cable and view the stream using any serial terminal (such as Termite), or transform the data in MATLAB during the printer's operation. The RX callback is set up but is not utilized. This introduces the opportunity for later firmware upgrades to allow the possibility of external commands being sent from a laptop for additional control. 

\subsection{SD Card Reading}
The printer reads motion commands from an SD card using the FatFs middleware over SPI communication (SPI1). Once FatFs is initialized and the file system is mounted, a command file, \texttt{PrintTask.csv}, is opened read with the \texttt{f\_open()} function.

During printer operation, the next commands (if the ISR queue has space) are read in the program's \texttt{while(1)} loop every 50~ms (20~Hz)task. The format of each command line in the CSV file is:
\[
X,\;Y,\;Z,\;\text{Speed},\;\text{ExtrusionRate},\;\text{Mode},\;\text{NozzleTemp},
\]
where \texttt{Mode} selects absolute (\texttt{0}) or relative (\texttt{1}) moves. Read command lines are queued into the ISR via \texttt{Stepper\_QueueAbs()} or \texttt{Stepper\_QueueRel()}.

\subsection{Switching Logic}
The printer switches its 12~V peripherals (nozzle heater, cooling fan, UV LED, and Peltier module) by controlling the logic levels of the gate terminals of their N-channel MOSFETs via the microcontroller. Upon startup, the Peltier gate (PB4) is driven high, keeping the cooler continuously on. The remaining three loads, are controlled via PWM through the STM32's timer channels:
\begin{itemize}
  \item Nozzle heater: \texttt{TIM3\_CH2} on \texttt{PB5}
  \item Fan: \texttt{TIM4\_CH1} on \texttt{PB6}
  \item UV LED: \texttt{TIM4\_CH2} on \texttt{PB7}
\end{itemize}
With $\text{PSC}=0$ and $\text{ARR}=4199$, each pulse width modulation channel operates at 20 kHz:
\begin{align*}
    f_\text{PWM} = \frac{f_\text{timer}}{(\text{PSC}+1)(\text{ARR}+1)} = \frac{84\text{ MHz}}{(\text{0}+1)(4199+1)} = 20\text{ kHz}.
\end{align*}
Duty cycles (0-100 \%) are updated in the \texttt{while(1)} loop every 50~ms by adjusting the channel compare register (CCR):
\begin{equation*}
 \mathrm{CCR} = \frac{\text{Duty Cycle}}{100}\,\mathrm{ARR}.
\end{equation*}
The blue LED undergoes a linear brightness modulation over a 10-second periodic interval (to show curing intensity adjustment capabilities) and the fan is set to operate at full intensity ($D=100\%$).

\section{Measurements and Results}
To verify nozzle heating and bed cooling, a FLIR ONE Pro camera captured the temperature distribution of both components (100\% duty cycle) after 10 minutes of operation, as shown in Figures~\ref{fig:nozdist} and~\ref{fig:beddist}. Due to an unavailability of hand-held thermocouple's in the M\&M Workshop during testing, a CASTALWARE digital thermometer was used to determine less accurate settling temperatures. By resting the end of the thermometer on the bed's centre, a minimum of $13~^\circ$C was recorded, and placing the probe in the E3D heater block's thermistor hole indicated a maximum of $230~^\circ$C.

\begin{figure}[H]
    \centering
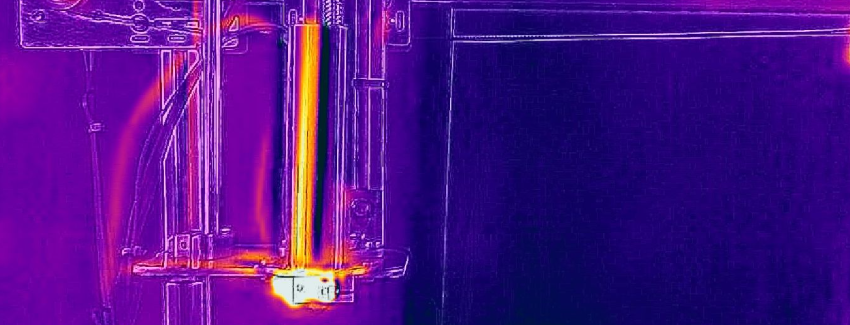
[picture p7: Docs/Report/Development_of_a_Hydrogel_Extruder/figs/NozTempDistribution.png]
    
    \caption{Nozzle temperature distribution after 10 minutes of being active (100\% duty cycle)}
    \label{fig:nozdist}
\end{figure}

\begin{figure}[H]
    \centering
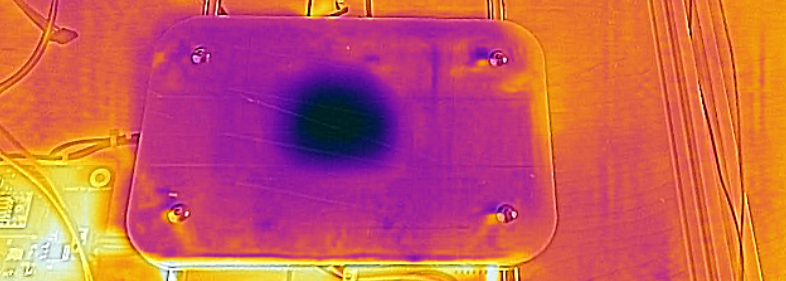
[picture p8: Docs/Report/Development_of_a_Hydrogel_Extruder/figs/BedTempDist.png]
    
    \caption{Bed temperature distribution after 10 minutes of being active }
    \label{fig:beddist}
\end{figure}

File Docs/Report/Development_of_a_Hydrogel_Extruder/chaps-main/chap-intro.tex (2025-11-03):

\chapter{Introduction}

\section{Background}

Tissue engineering is a relatively new field within the multidisciplinary realm of biomedical engineering. It combines the fields of biology, medicine, material science, and engineering into a single discipline in which three-dimensional structures are fabricated with the intention of restoring, maintaining, or even improving the function of tissue. The art of engineering tissue has many applications within medicine, cosmetics, and cellular research, and there are many methods of fabricating these tissue scaffolds, with one common approach being 3D printing.

The ability to create structures that replicate tissue functions, whether seeded with cells or not, has countless applications within various fields such as medicine, cosmetics, and biological research. It creates the potential to manufacture substitute tissues (or even organs in more advanced applications) in regenerative medicine for transplantation to mimic the function of damaged or missing tissues in patients. It is often used in drug development and testing. Tissue engineering is also used in biological research, where 3D environments are created to simulate and study the growth and behaviour of cellular systems such as cancer cells and bacteria.

A popular class of materials used to fabricate substitute tissue structures are hydrogels, which can be processed in various ways, with 3D printing being a particularly popular method. Hydrogels are a broad class of materials that are known for their tunable properties, porous nature, and ability to retain large amounts of water, which allows many hydrogels to support cell growth. However, due to the complex rheological properties of different hydrogels and the varying methods by which these materials are hardened, it remains a challenge to 3D print complex structures in a way that is accurate, repeatable, and cost-effective. This project aims to design, develop, and test an extrusion system capable of creating 3D hydrogel scaffolds to overcome these challenges.

\section{Objectives}

The primary objectives of this project are:
\begin{enumerate}
    \item To design and assemble a hydrogel extruder capable of controlled and stable extrusion.
    \item To design and construct a three-axis gantry to position the extruder for accurate 3D printing.
    \item To design and implement an embedded system, including necessary firmware, capable of real-time control of system actuators, sensing, and closed-loop logic.
    \item To experimentally tune and validate the mechatronic system through a designed calibration procedure for determining optimal printing parameters for different bioinks.
\end{enumerate}

The scope of the project is limited to developing and demonstrating a working prototype. While the system is not intended to achieve the full performance and quality of commercial bioprinters, it provides a validated platform for future upgrades and serves as a tool for characterising bioinks.

\section{Motivation}

The motivation for this project lies in the growing importance of tissue engineering and the need for accessible tools to support research in this field. Most commercial bioprinters remain prohibitively expensive and proprietary, limiting their availability to smaller research groups. Developing a low-cost prototype capable of producing controlled, stable, and repeatable prints allows research in tissue engineering to be conducted by a wider range of researchers. This project therefore contributes to making tissue engineering more affordable and while providing a means of characterising different gels, offering insight into their behaviour in both tissue engineering and other biomedical applications.

\section{Use of AI}
The use of AI tools in this project was limited to identifying and correcting minor technical writing errors, including grammar, spelling, and punctuation. All technical aspects of the project, including the literature review, design, and experimental analysis, were independently performed.

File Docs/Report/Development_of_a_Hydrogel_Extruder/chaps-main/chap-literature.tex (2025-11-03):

\chapter{Literature review}

\section{Tissue engineering}
\subsection{Definition and Background of Tissue Engineering}
Tissue engineering can be defined as the “the application of principles and methods of engineering and life sciences toward fundamental understanding of structure–function relationships in normal and pathological mammalian tissues and the development of biological substitutes to restore, maintain, or improve tissue function” \citep{skalak_1988}.

The concept of replacing dysfunctional tissues and organs has been around for millennia, with the first nose transplants occurring as early as 1000 B.C. in ancient India \citep{saltzman_2004}. In recent centuries, major advances in organ transplantation have taken place – even transplants of organs supplied by donors. These strides include tooth transplants, successful skin grafts (which became commonplace in the 1800s), and even the first successful heart transplant which took place in South Africa, 1967 \citep{saltzman_2004}.

Despite the rapid advancements in organ transplantation in recent centuries, all transplants involving organs from donors have a common issue. The problem is that the tissue/organ in need of replacement requires the availability of viable tissues or organs from a donor and in modern times the demand for tissue/organ replacement far exceeds the available supply from donors \citep{saltzman_2004}. This problem can be alleviated using tissue engineering. 

Through tissue engineering, the demand for useable and available donor tissues is mitigated by creating viable tissues (and even organs) through artificial means. This replacement tissue is formed by creating a three-dimensional scaffold to take on the shape of the space of the human (or organism) that needs to be filled with new tissue. These scaffolds can be acellular or seeded with cells prior to formation. The acellular scaffolds rely on the body’s natural ability to regenerate the cells for normal function. Whether seeded or regenerated from the body, the scaffolds (with its contained cells) are intended to replace the functionality of the old or damaged tissue \citep{olson_2011}.

\subsection{Scaffold Requirements}
The main purpose of artificial scaffolding in tissue engineering is to mimic the environment and behaviour of the tissue being replaced. To create artificial scaffolding that recreates these same conditions, the scaffolding needs to be biocompatible, biodegradable, have sufficient architecture and have the same mechanical properties as the native extracellular matrix \citep{obrien_2011}.

The scaffolds must be biocompatible with the cells. This means that the cells should be able to migrate through the scaffold material and be able to function normally within this artificial EM (extracellular matrix). This criterion also means that the engineered tissue should result in minimal immune response from the body once it is integrated (or implanted) with the host tissue \citep{obrien_2011}.

The artificial scaffolds must be biodegradable since the scaffolds are not meant to be permanent implants. The scaffolds are intended to be gradually broken down and slowly replaced with a new extracellular matrix that is formed by the seeded or host’s natural cells. To ensure that the tissue continues to function normally and remain undamaged, the by-products of the scaffold’s degradation must be non-toxic \citep{obrien_2011}.

The architecture of the scaffolds should be sufficient to allow for the cells to exist inside the matrix. This means that it should have an interconnected porous structure, and it should be highly porous. The reason for this, is so that the structure can allow for the diffusion of nutrients to the cells and the diffusion of waste products from the cells through the EM \citep{obrien_2011}.

The scaffold’s mechanical properties should match that of the native extracellular matrix or that of its intended purpose. This involves selecting materials (for scaffolding) that have similar stiffness (Young’s modulus), hardness, etc. The importance of matching mechanical properties to the scaffolding can differ depending on what the engineered tissues intended purpose is. For example, if its function includes a structural role (as would be the case with bones and cartilage), then it is important to ensure it has enough stiffness and strength to not break upon usage. It should also be noted that the artificially formed matrix should have sufficient mechanical properties for it to remain undamaged when being implanted. In addition to this, it is important to ensure that the scaffold’s mechanical properties do not get chosen at the cost of the scaffold porosity as this can result in the engineered tissue having difficulty in allowing vascularization and cell infiltration resulting in conditions where the cells cannot exist over time \citep{obrien_2011}.

\subsection{Scaffold Fabrication Methods}
There are many methods of fabricating scaffolds. These techniques for creating scaffolds differ according to the material used to create the scaffold and depending on whether the seeded cells can survive the scaffolding formation process. The formation process also needs to ensure that the produced scaffolds meet the requirements for being used as engineered tissue (it must be biocompatible, porous, etc.). These varying methods can be split up into conventional and advanced methods \citep{dutta_2017}.

Conventional techniques include particulate-leaching, extrusion, molding, thermally induced gelation, gas foaming, etc. \citep{dutta_2017}. These processes can be used in combination to manufacture scaffoldings that meet the previously identified scaffold criteria and can work together to form more advanced manufacturing techniques.

Advanced methods include 3D printing, electrospinning, emulsion templating, and designed self-assembling peptides:

\begin{itemize}
  \item 3D printing allows for the computer aided design of scaffolding and then the formation of these designs through additive manufacturing methods such as Fused Deposition Modelling, Stereolithography, and Laser Sintering; this style of fabrication is particularly useful for rapid prototyping, developing scaffolds with complex geometries, and having control over the macroscopic properties of the artificial matrix structure \citep{dutta_2017}. 
  \item Electrospinning involves using an extruder with an electric field to produce ultrafine nanofibers to form the extracellular matrix; this method is very useful for creating scaffolds with fibrous nanoporous materials with high precision \citep{dutta_2017}. 
  \item Emulsion templating uses phase separation to form tertiary pores to create scaffolds with a hierarchical pore structure; emulsion templating is useful for creating scaffolds with a porosity gradient \citep{dutta_2017}. 
\end{itemize}

\subsection{Scaffold Materials}
The material used to form the extracellular matrix depends on the application of the tissue that is being engineered. These possible materials include linear aliphatic polyesters and other synthetic polymers, natural macromolecules, inorganic materials, and hydrogels \citep{mapx2004}.

Linear aliphatic polyesters, such as PGA and PLA, are a group of biodegradable plastics that break down due to the hydrolysis of ester bonds. There are also other synthetic materials such as PPF and tyrosine-derived polymers that are used in bone engineering \citep{mapx2004}.

Natural macromolecules, like proteins polysaccharides, are often used in tissue engineering. Examples of fibrous proteins that are used to create tissue is collagen and silkworm silk. Collagens have useful properties and is therefore often used as a major component of EM scaffolding although it has potential issues with pathogen transmission and less controllable biodegradability; silk (from silkworms) is a useful tissue replacement option in certain instances due to its desirable tensile properties but has issues with cytotoxicity and slow degradation. Polysaccharides such as alginate, chitosan, and hyaluronate (these examples are or can be used to create hydrogels) are also useful in creating porous solid-state scaffolds \citep{mapx2004}.

Inorganic materials that fall into the categories of porous bioactive glasses and calcium phosphates are used in the fields of bone and mineralized tissue engineering as they support the adhesion, growth, and differentiation of cells \citep{mapx2004}.

Hydrogel polymers (like PEGs, alginates, etc.) are also a desirable option for producing extracellular scaffolds because they can be easily made to form structures of complex shapes/geometries, they can be seeded with cells, have solidification rates that are controllable (to some degree) and can often be implemented through procedures that are minimally invasive \citep{mapx2004}.

\section{Hydrogel}

\subsection{Introduction to Hydrogels}
Hydrogels are three-dimensional polymeric networks that are hydrophilic and therefore capable of containing large quantities of water while keeping their structural integrity \citep{peppas_2000}. Hydrogels have many desirable properties that make it useful in many applications (even outside of tissue engineering).

The network structure of hydrogels is comprised of homopolymer or copolymer chains. These chains attract water, but the overall polymer network is still insoluble due to chemical and/or physical (entanglements, crystallites, etc.) crosslinks. Crosslinks are the tie points where the adjacent or neighboring chains are joined together. These crosslinks allow for the network structures to be solid and have some degree of structural integrity \citep{peppas_2000}.

Hydrogels can be used in many applications. Due to their resemblance to the properties of natural extracellular matrices of tissue (as they are porous, enzymatically degradable, soft in consistency, biocompatible, and have high water content), they are an attractive option for applications within the medical and pharmaceutical sectors. Their biocompatibility (contributed to by its capacity to hold large amounts of water) allows it to make contact lenses, biosensor membranes, artificial heart lining, artificial skin materials, and drug delivery systems \citep{peppas_2000}.

\subsection{Classification of Hydrogels}
Hydrogels can be classed in many ways and there are many kinds of hydrogels with different applications within the fields of medicine or tissue engineering.

Hydrogel can be classified according to its polymer source, physical properties, ionic charge, biodegradability, or its method of crosslinking. With regards to classifying these gels according to their source, they can either be natural, synthetic, or hybrid polymer hydrogels \citep{liwu2020}. 

Natural hydrogels are a form of natural polymer (or biopolymer) as they are derived from organisms. These can be further classed into polysaccharide hydrogels (such as alginate which comes from brown algae), glycosaminoglycan hydrogels, and polypeptide/protein hydrogels (the most common example of these include collagen and gelatin hydrogels) \citep{liwu2020}.

Synthetic hydrogels are artificially created and come in the form of polyacrylamide (PAAm), poly(ethylene glycol) (PEG), and poly(vinyl alcohol) (PVA) hydrogel. PEG derived gels are the most used synthetic hydrogels in medicine due to their hydrophilic nature and excellent biocompatibility \citep{liwu2020}.

Hybrid hydrogels are made from a combination of natural and synthetic materials. The reason for this is that synthetic and natural gels on their own tend to have limited mechanical strength but through the combination of natural and synthetic materials this problem is rectified to allow improved and tunable mechanical properties as well as allow for the addition of other desirable characteristics to the gel product \citep{liwu2020}.

\subsection{Properties of Hydrogels}
Since there are countless types and forms of  hydrogel, in this section, the properties of specific examples of hydrogels, relevant to the context of extrusion-based 3D printing with the intention of engineering tissue, are considered. These examples are GelMA (gelatin methacrylate), PEGDA (poly(ethylene glycol) diacrylate), Alginate, and Matrigel.
\begin{itemize}
  \item Biocompatibility – all four of these hydrogels are highly biocompatible but only some are naturally able to adhere to cells. GelMA and Matrigel support cell adhesion; PEG-based hydrogels and Alginate naturally have poor cell adhesion, and this can be rectified by incorporating cell-adhesive peptides \citep{liwu2020}.
  \item Biodegradability – GelMA, Alginate, and Matrigel are enzymatically degradable. If the necessary enzymes are not available to degrade Alginate,  it can also be ionically degraded while immersed in an aqueous solution with Na\(^+\) ions. PEG-based gels are not degradable and need to be chemically modified to become biodegradable \citep{liwu2020}.
  \item Water retention – PEGDA, GelMA, and Alginate are all very soluble (in water and other solvents) and capable of holding large amounts of water \citep{liwu2020}. Matrigel needs to be chilled for it to be more easily soluble \citep{merceron_2015}.
  \item Crosslinking method – PEGDA and GelMA (with a photoinitiator) are made to cure via photo crosslinking when irradiated by UV rays. Alginate is ionically crosslinked by divalent cations like Ca\(^{2+}\) \citep{liwu2020}. Matrigel, however, is thermally crosslinked (which is reversable). It is a liquid at low temperatures (around 4 °C), and it forms a solid matrix at higher temperatures of around 37 °C \citep{merceron_2015}.
  \item Rheological properties – the rheological properties of hydrogels often depend on its temperature, concentration is a solute, and molecular weight. Before gelation, PEGDA is found to be a Newtonian fluid (to a certain shear flow rate) and its viscosity increases as its molecular weight increases \citep{brikov_2016}. Both GelMA and Alginate, on the other hand, are non-Newtonian fluids that exhibit shear-thinning behaviour, meaning that their viscosity reduces as its shear rate increases \citep{gregory_2022}. The viscosity of GelMA also varies depending on temperature and concentration. Its viscosity decreases as its temperature increases and its concentration decreases. The viscosity of GelMA, therefore, is very low when flowing at temperatures above \(30\,\,^{\circ}\mathrm{C}\) (significantly less than \(1\,\,\mathrm{Pa \cdot s}\)), but at cooler temperatures (less than \(30\,\,^{\circ}\mathrm{C}\)) its viscosity drastically increases \citep{adhikari2021photoinduced}. For example, a solution with the GelMA concentration of 10\% at \(26\,\,^{\circ}\mathrm{C}\) has a viscosity of roughly \(168\,\,\mathrm{Pa \cdot s}\), which is a very large increase in viscosity \citep{cellink_gelma_2020}.

\end{itemize}

\section{3D Printing Hydrogel}
As extrusion-based 3D printing has continued to grow as a method of engineering tissues with hydrogel, many companies have developed state-of-the-art hydrogel 3D printers for biomedical applications. The most advanced and notable bioprinters of today include the CELLINK BIO X printers, the RegenHU 3DDiscovery™ Evolution, and the Allevi 3 printer. To get an idea of the state of the art of hydrogel printers, this subsection will discuss the capabilities of the BIO X printer.

The BIO X 3D printer is developed by a company called CELLINK. It is capable of extruding and printing with many kinds of bioinks including GelMA, PEGDA, Alginate, etc. for application in biomedical research and has a print resolution of 1 µm \citep{biox_brochure}. 

The BIO X has interchangeable and attachable printheads for different forms of gel extrusions including a pneumatic, syringe pump, thermoplastic and inkjet printheads. The printing bed and printheads are temperature controlled (to account for the wide-ranging rheological properties of different hydrogels). The printers also include UV LED attachments for photo-induced crosslinking and implement a UV ray-based system (with smaller wavelengths than for curing) for sterilizing the printing environment in between prints to ensure biosafety standards are met \citep{biox_brochure}.

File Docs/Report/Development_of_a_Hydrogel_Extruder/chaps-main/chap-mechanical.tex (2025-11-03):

\chapter{Mechanical Design}

This chapter covers the mechanical design of the hydrogel bioprinter using the standard engineering design process that involves the identification of both stakeholder and engineering requirements, concept generation and selection, and the final design. The 3D printer system must fulfil two primary functions:
\begin{itemize}
    \item Extrude hydrogel (specifically GelMA).
    \item Position the extruder in 3D space.
\end{itemize}

\section{Stakeholder Requirements}

The development of the hydrogel bioprinter is performed in accordance to the purpose of its use and the needs of its stakeholders. The 3D printer is being developed to serve as a research tool for SU's Physiology Department, in which it will be used as an apparatus for characterising bioinks and creating hydrogel scaffolds (acellular or seeded with cells) to model and simulate cellular growth in biomedical research. The stakeholders whose needs guide the design of the system include the physiology researchers (end-users), the engineering student developing the printer, regulatory authorities that require compliance with health and safety standards as well the strict sanitary standards that need to be met in biomedical research, and Stellenbosch University by which the project is funded. While not strictly a mandatory requirement, the system should also meet the needs of any future designer that is tasked with upgrading the system or adding additional functionalities to the printer. The requirements that the system must/should meet in order to fulfil the needs of these stakeholders are tabulated below in Table~\ref{tab:stakeholder_requirements}.
\vspace{5cm}
\small
\begin{longtable}{|c|m{2.2cm}|m{7.3cm}|c|}
\caption{Stakeholder Requirements}
\label{tab:stakeholder_requirements} \\
\hline
\textbf{No.} & \textbf{Stakeholder} & \textbf{Description} & \textbf{Priority} \\
\hline
\endhead
\hline
SR1 & Researchers (End-users) & The system must be able to extrude hydrogel to create 3D hydrogel scaffolds & must-have \\
\hline
SR2 & Designer (Engineer) & The printer should be able to precisely, accurately, and smoothly adjust the position of the extruder in 3D space\textsuperscript{1} & must-have \\
\hline
SR3 & Designer (Engineer) & The extruder must be able to accurately and precisely control the flow rate of hydrogel being extruded\textsuperscript{1} & must-have \\
\hline
SR4 & Researchers (End-users) & The system should support the real-time gelation of the bioink during print tasks\textsuperscript{2} & must-have \\
\hline
SR5 & Researchers (End-users) & The bioprinter should support multiple types of hydrogel\textsuperscript{3} & must-have \\
\hline
SR6 & Researchers (End-users) & The printer should have a repeatable performance for unique set of parameters\textsuperscript{1} & must-have \\
\hline
SR7 & Researchers (End-users) & The printer must allow for tunable parameters\textsuperscript{3} & must-have \\
\hline
SR8 & Researchers (End-users) & The system should be user-friendly and simple to operate\textsuperscript{4} & must-have \\
\hline
SR9 & Biosafety Authorities & The extruder must be sterilisable and come with a documented cleaning procedure\textsuperscript{5} & must-have \\
\hline
SR10 & Health and Safety Authorities & The system should be safe to handle with minimized risks to the health and safety of its users & must-have \\
\hline
SR11 & SU's finance department & The printing system as a whole should be affordable and meet budget requirements\textsuperscript{6} & must-have \\
\hline
SR12 & Researchers (End-users) & The system must include a documented experimental procedure to calibrate the bioprinter to perform optimised prints of desired bioinks\textsuperscript{3} & must-have \\
\hline
SR13 & Researchers (End-users) & The system should be able to transmit real time experimental data\textsuperscript{3} & optional \\
\hline
SR14 & Designer (Engineer) & The printer should include feedback control for precise operation & optional \\
\hline
SR15 & Future Designers & The printer should be modular and allow for future upgrades\textsuperscript{7} & optional \\
\hline
\end{longtable}
{\footnotesize
\noindent\textsuperscript{1} The calibrated printer should perform prints that accurately match the desired print tasks and do not vary across iterations with a specific set of printer settings.

\noindent\textsuperscript{2} This means that the printer should support the solidification of the gel during print operations to ensure the structural integrity of printed scaffolds.

\noindent\textsuperscript{3} These requirements are needed for the system to fulfil its role in serving as a tool for characterising bioinks and calibrating the printer to perform optimised prints.

\noindent\textsuperscript{4} The end-users are not engineers and the printer should therefore be simple to operate by researchers without technical knowledge of mechatronic systems.

\noindent\textsuperscript{5} The printer must be cleaned and sterilised throughout its lifetime to ensure bioink viability and compliance with health standards.

\noindent\textsuperscript{6} This excludes resources that will be sourced from within the University of Stellenbosch.

\noindent\textsuperscript{7} Future upgrades may include adding a user interface or developing an additional extruder for dual extrusion.
}

\section{Engineering Requirements}
The needs of the stakeholders must be translated into engineering requirements that define how the system will meet these needs.

Tables~\ref{tab:func_requirements} and~\ref{tab:nonfunc_requirements} list the FRs and NFRs respectively.

\small
\begin{longtable}{|c|m{8.1cm}|l|}
\caption{Functional Requirements} 
\label{tab:func_requirements} \\
\hline
\textbf{No.} & \textbf{Description} & \textbf{Related SR} \\
\hline
\endfirsthead
\hline
\textbf{No.} & \textbf{Description} & \textbf{Related SR} \\
\hline
\endhead
FR1 & The printer must be able to move the extruder along three axes (relative to a printing platform) with precise positional control. & SR2, SR6 \\
\hline
FR2 & The system must extrude hydrogel at a desired and controlled flow rate. & SR1, SR3 \\
\hline
FR3 & The printer must have the ability to include UV curing with adjustable intensity that operates during extrusion. & SR4 \\
\hline
FR4 & The printer must include the ability to adjust bioink fluid properties by bed and nozzle temperature control. & SR7, SR9 \\
\hline
FR5 & The printer firmware must allow for the adjustment of printer parameters such as nozzle and bed temperature, extrusion speed, and travel speed. & SR7 \\
\hline
FR6 & The system should be able to transmit sensory feedback for system control and to capture real-time data during the printer's calibration. & SR13, SR14 \\
\hline
FR7 & The printer must include feedback control for precise operation. & SR14 \\
\hline
\end{longtable}

\small
\begin{longtable}{|c|m{8.1cm}|l|}
\caption{Non-Functional Requirements}
\label{tab:nonfunc_requirements} \\
\hline
\textbf{No.} & \textbf{Description} & \textbf{Related SR} \\
\endfirsthead
\hline
\hline
\textbf{No.} & \textbf{Description} & \textbf{Related SR} \\
\hline
\endhead
\hline
NFR1 & The extruder/bioink fluid path must be removable and capable of being cleaned and sterilised. & SR9 \\
\hline
NFR2 & The printer should be modular to support future upgrades. & SR15 \\
\hline
NFR3 & The printer must be affordable and within the allocated SU final year project budget. & SR11 \\
\hline
NFR4 & The design, development, and use of the bioprinter must comply with Stellenbosch University's health and safety regulations. & SR10, SR11 \\
\hline
NFR5 & The system should be user-friendly and simple to operate. & SR8 \\
\hline
NFR6 & The bioprinter should support multiple types of hydrogel. & SR5 \\
\hline
NFR7 & The system must include a documented procedures to calibrate the bioprinter to desired hydrogels and clean after use & SR9, SR12 \\
\hline
\end{longtable}

The performance requirements, documented in Table~\ref{tab:performance_requirements}, quantify how well the system must meet its functional requirements. The target levels for each performance requirement was chosen to match the performance capabilities of the current state of the art for bioprinters (such as the Bio X) as far as reasonably possible.

\small
\begin{longtable}{|c|m{5.5cm}|c|c|c|m{1.5cm}|}
\caption{Performance Requirements}
\label{tab:performance_requirements} \\
\hline
\textbf{No.} & \textbf{Description} & \textbf{Target} & \textbf{Range} & \textbf{Unit} & \textbf{Related FR} \\
\hline
\endfirsthead
\hline
\textbf{No.} & \textbf{Description} & \textbf{Target} & \textbf{Range} & \textbf{Unit} & \textbf{Related FR} \\
\hline
\endhead
PR1 & Extrusion speed\textsuperscript{1} & 5 & 1 - 10 & mm/s & FR2 \\
\hline
PR2 & Positional accuracy along XY axes\textsuperscript{2} & 100 & 1 - 500 & $\mu$m
 & FR1 \\
\hline
PR3 & Positional accuracy along Z axis\textsuperscript{2} & 50 & 1 - 100 & $\mu$m
 & FR1 \\
\hline
PR4 & Maximum travel speed along XY axes\textsuperscript{1} & 10 & 0 - 50 & mm/s & FR1 \\
\hline
PR5 & Minimum bed temperature\textsuperscript{3} & 4 & < 20 & $^{\circ}$C & FR4 \\
\hline
PR6 & Maximum nozzle temperature\textsuperscript{4} & 85 & 80 < & $^{\circ}$C & FR4 \\
\hline
PR7 & Nozzle temperature control tolerance & $\pm$ 1 & $\pm$ 0.5 – 2 & $^{\circ}$C & FR4 \\
\hline
PR8 & Extrusion force control tolerance & $\pm$ 5 & $\pm$ 2 – 10 & \% & FR2, FR7 \\
\hline
\end{longtable}
{\footnotesize
\noindent\textsuperscript{1} Recommended print speed of 0-10 mm/s for the BIO X \citep{cellink_biox_manual_2023}.

\noindent\textsuperscript{2} The Bio X has a 1~µm XY/Z positional accuracy \citep{biox_brochure}.

\noindent\textsuperscript{3} This matches the Bio X's minimum bed temperature capability of 4 $^{\circ}C$ \citep{biox_brochure}.

\noindent\textsuperscript{4} The target matches the maximum capability of the Bio X's pneumatic print heads \citep{biox_brochure}.
}
\section{Extruder Design}
The rest of this chapter will cover the design of each of the bioprinter’s subsystems, using a concept generation and selection process, followed by the final design. Since the system’s two primary functions are to extrude gel and position the extrusion nozzle in 3D space, these functions serve as the basis for dividing the system into its respective subsystems (extruder and gantry). This section focuses on the extruder design, starting with the development of generated concepts.

\subsection{Concept Generation}
\subsubsection*{Concept 1}
The first concept, shown in Figure~\ref{fig:pumpConcept}, illustrates a pump-based extruder design in which a peristaltic pump is used to drive the continuous flow of non-gelled bioink from a fluid reservoir. The reservoir could take the form of either a permanent or intermediate temporary storage for the gel ink (configured to create the correct handling conditions) and not necessarily in the beaker-shaped form shown in the figure.

\begin{figure}[H]
    \centering
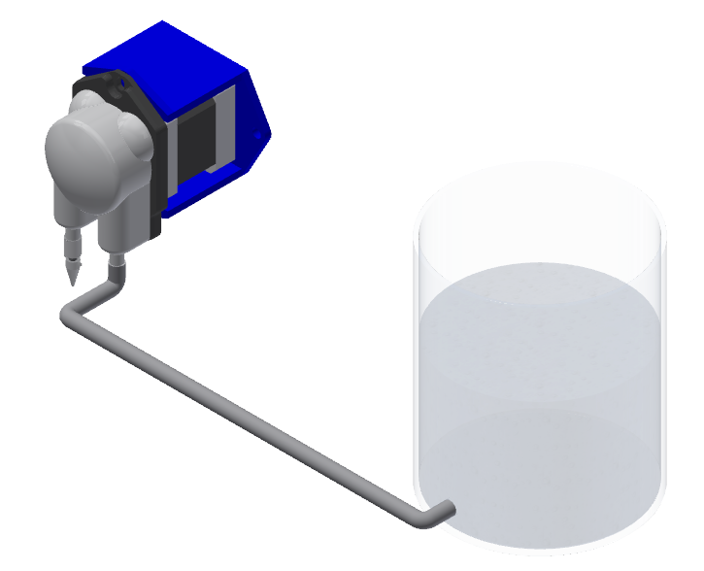
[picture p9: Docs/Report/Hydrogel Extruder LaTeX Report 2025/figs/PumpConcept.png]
    
    \caption{Concept 1 Pump-Based Extruder Design}
    \label{fig:pumpConcept}
\end{figure}

\subsubsection*{Concept 2}
Figure~\ref{fig:syringeConcept1} shows the second concept is an assembly, in which a stepper motor drives two lead screws (through a system of gears) to push a plunger further into a syringe. The pre-existing syringe is easily removable by either unbolting the flanged tube in which the syringe sits or by sliding the syringe out vertically when the platform that pushes the plunger is in its uppermost position. The inclusion of gears is used to allow the plunger to be driven with a greater force magnitude for extruding high-viscosity gels through small-diameter nozzles.

\begin{figure}[H]
    \centering
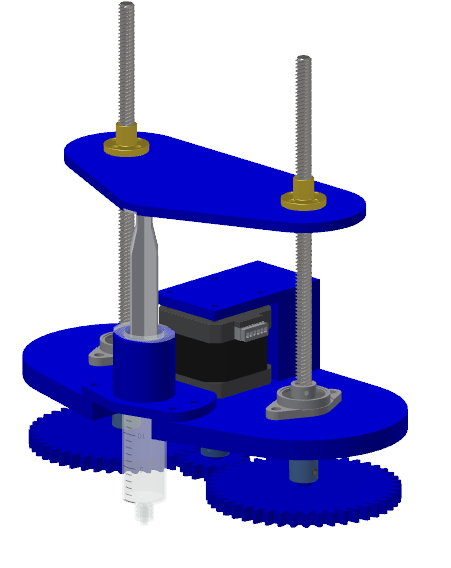
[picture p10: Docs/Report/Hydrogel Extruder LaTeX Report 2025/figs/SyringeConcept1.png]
    
    \caption{Concept 2 Syringe-Based Extruder Design}
    \label{fig:syringeConcept1}
\end{figure}

\subsubsection*{Concept 3}
The final concept, in Figure~\ref{fig:syringeConcept2}, shows another syringe-based extruder similar to the second concept. This concept deviates from the previous one with regards to its frame and actuation style. This concept uses a syringe with a threaded nozzle to accept screw-in component additions (for added modularity). The extruder uses a belt-and-pulley drive-train to increase the force of the lead screw on the plunger and also uses a shaft to guide the plunger-driving platform.
\begin{figure}[H]
    \centering
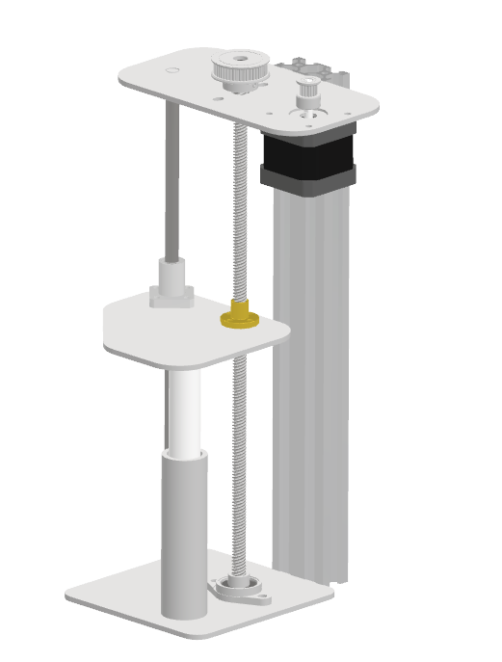
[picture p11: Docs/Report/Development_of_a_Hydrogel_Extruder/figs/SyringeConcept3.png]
    
    \caption{Concept 3 Custom Syringe-Based Extruder Design}
    \label{fig:syringeConcept2}
\end{figure}

\subsection{Concept Evaluation and Selection}
To objectively evaluate the three generated concepts and identify the one that best satisfies the project’s stakeholder requirements, a Pugh chart was developed. This method compares each concept against multiple weighted criteria, each derived from a specific stakeholder requirement. Concept 2 was selected as the reference datum, and the other concepts were rated relative to it on a scale from –2 to +2, with positive values indicating favourable performance and negative values indicating less favourable performance. Table~\ref{tab:pugh1} presents the results of the Pugh chart evaluation.

\begin{sidewaystable}[p]
\centering
\caption{Concept Evaluation (Pugh Chart)}
\label{tab:pugh1}
\renewcommand{\arraystretch}{1.2}
\setlength{\tabcolsep}{3.5pt}

\begin{tabular}{|>{\centering\arraybackslash}p{35mm}|
                >{\centering\arraybackslash}p{15mm}|
                >{\centering\arraybackslash}p{15mm}|
                >{\raggedright\arraybackslash}p{35mm}|
                >{\centering\arraybackslash}p{15mm}|
                >{\raggedright\arraybackslash}p{35mm}|
                >{\centering\arraybackslash}p{15mm}|
                >{\raggedright\arraybackslash}p{35mm}|}
\hline
\multicolumn{2}{|c|}{\textbf{Criterion}} &
\multicolumn{2}{c|}{\textbf{Concept 1}} &
\multicolumn{2}{c|}{\textbf{Concept 2}} &
\multicolumn{2}{c|}{\textbf{Concept 3}} \\
\hline
\textbf{Description} & \textbf{Weight} &
\textbf{Rating} & \textbf{Motivation} &
\textbf{Datum} & \textbf{Motivation} &
\textbf{Rating} & \textbf{Motivation} \\
\hline
Maximum flow rate (SR1) & 0.07 & +2 & Higher throughput & 0 & Limited by lead screw and drive-train & 0 & Limited by lead screw and drive-train\\\hline
Maximum extrusion force (SR1) & 0.13 & -2 & Head losses due to longer fluid path & 0 & High due to drive-train & 0 & High due to drive-train \\\hline
Ink storage volume (SR1) & 0.05 & +2 & Large reservoir and continuous pump action & 0 & Limited by syringe volume & 0 & Limited by syringe volume \\\hline
Flow rate accuracy (SR3) & 0.19 & -1 & Inaccurate at low speeds & 0 & Accurate due to lead screw and gear reduction & 0 & Accurate due to lead screw and drive-train \\\hline
Repeatable performance (SR6) & 0.15 & -1 & Tube ageing & 0 & Variable backlash from printed gears & +2 & Low backlash from tensioning \\\hline
Sterilisability and cleanability (SR9) & 0.13 & -2 & Hard to clean long path & 0 & Removable syringe and straight path & 0 & Removable syringe and straight path \\\hline
Affordability (SR11) & 0.15 & -2 & Requires a peristaltic pump & 0 & Standard parts & 0 & Standard parts \\\hline
\hline
\multicolumn{2}{|l|}{\textbf{Sum of plus ratings}} &
\multicolumn{2}{c|}{4} &
\multicolumn{2}{c|}{0} &
\multicolumn{2}{c|}{2} \\\hline

\multicolumn{2}{|l|}{\textbf{Sum of minus ratings}} &
\multicolumn{2}{c|}{-8} &
\multicolumn{2}{c|}{0} &
\multicolumn{2}{c|}{0} \\\hline

\multicolumn{2}{|l|}{\textbf{Overall total}} &
\multicolumn{2}{c|}{-4} &
\multicolumn{2}{c|}{0} &
\multicolumn{2}{c|}{2} \\\hline

\multicolumn{2}{|l|}{\textbf{Weighted total}} &
\multicolumn{2}{c|}{-0.92} &
\multicolumn{2}{c|}{0} &
\multicolumn{2}{c|}{0.30} \\\hline

\end{tabular}
\end{sidewaystable}

The Pugh chart indicates that Concept 3 provides the most favourable balance across the weighted criteria. Its lead screw and drive-train increases flow rate accuracy and extrusion force. Although scoring similarly to Concept 2 in most categories, its addition of belt tensioning means greater extrusion accuracy due to reduced backlash. These factors enable the extruder to handle highly viscous gels with repeatable performance while maintaining sterilisability.

\subsection{Final Extruder Design}
With Concept 3 selected as the most suitable option, the concept is refined into a final extruder design that is ready for assembly. In this subsection, the extruder is specified in detail, with calculations provided to quantify its design requirements (stepper torque, pulley ratios, and plunger dimensions) and to determine its theoretical performance characteristics such as flow rate resolution. These demonstrate that the final design meets the stakeholder requirements.
\subsubsection*{Extrusion Force Calculations}
To calculate the needed stepper torque and pulley ratio, it is first necessary to describe the system characteristics and requirements. The syringe should hold roughly \SI{25}{mL} and therefore has an inner diameter of \SI{20}{mm} and an \SI{80}{mm} length. The nozzle’s threaded shank provides attachment for an E3D hot-end assembly that can accommodate different nozzle diameters. To be conservative and to allow printing with high accuracy, the design assumes the ability to extrude through a minimum nozzle diameter of \SI{0.2}{mm} with an approximate length of \SI{20}{mm}. To ensure compatibility with multiple hydrogels, the extruder is specified to handle gels with a maximum viscosity of $1~\si{\pascal\second}$ to match GelMA's viscosity above $30~^\circ$C.

These assumptions are restated in Appendix~A.1, which shows, using Poiseuille’s Law, that extrusion under these edge-case conditions requires the plunger to deliver a maximum pressure of $181.3~\si{\kilo\pascal}$. The calculations further indicate that, to achieve this pressure over the cylinder’s cross-sectional area, the lead screw must apply approximately \SI{60}{N} of force on the plunger. With a safety factor of 5, \SI{300}{N} corresponds to a torque requirement of $0.638~\text{N}\cdot\text{m}$ for the TR8$\times$8 lead screw. To achieve this, a NEMA17 stepper motor with a maximum holding torque of $0.28~\text{N}\cdot\text{m}$ is used in combination with a 3:1 GT2 pulley reduction (48T:16T), increasing the maximum torque at the lead screw to $0.84~\text{N}\cdot\text{m}$.

\subsubsection*{Flow Rate Resolution}
The minimum flow rate resolution without microstepping can be determined based on the relationship between the angle of the motor shaft, lead screw pitch, and the cross-sectional area inside the syringe. Since the system uses a pulley ratio (PR) of 3:1, the lead is \SI{8}{mm}, and the motor is adjusted by $1.8^{\circ}$ per full step, the positional accuracy with which the plunger can move is:

\begin{align*}
\Delta x_{\text{Full Step}} &= \frac{\text{Lead}}{\text{PR}} \times \frac{\theta_{\text{Full Step}}}{360^{\circ}} \\
&=\frac{8.00}{3}\times \frac{1.8^\circ}{360^\circ} \\
&= 0.0133~\text{mm}/\text{step}.
\end{align*}

\noindent To convert this to a volumetric resolution, this value must be multiplied by the area of the syringe's cross-section through which the plunger slides:
$$\Delta V_\text{Full Step} =\pi \left(10 \times 10^{-3}\right)^2 (1.33 \times 10^{-5})=4.19\times10^{-9} \,\,\text{m}^3/\text{step} =\boxed{4.19~\mu\text{L}/\text{step}} .
$$
Therefore, the extruder has a minimum theoretical extrusion resolution of $4.19~\mu\text{L}$ for a full step that drives the stepper. This resolution can be further refined through microstepping.

\subsubsection*{Buckling Analysis}
The syringe plunger is made of PVC, and the minimum diameter of the plunger stem must be determined to avoid buckling under the extrusion-force edge case of \SI{300}{N}. According to \cite{callister2018materials}, the modulus of elasticity of PVC ranges from \SI{2.41}{\giga\pascal} to \SI{4.14}{\giga\pascal}. Therefore, taking the modulus of elasticity as \SI{2.41}{\giga\pascal} and considering that the plunger stem length is \SI{80}{mm} (to allow full range of motion in the syringe), the minimum diameter can be determined with the Euler buckling formula and the area moment of inertia for a circular cross-section:
\[
P_{cr} = \frac{\pi^{2} E I}{(K L)^{2}}, 
\quad \text{and} \quad 
I = \frac{\pi d^{4}}{64},
\]
\[
\Longleftrightarrow
\; d = \left( \frac{64 P (K L)^{2}}{\pi^{3} E} \right)^{\tfrac{1}{4}}.
\]

For this derived formula for the stem’s minimum diameter, it is further noted that the design includes parts that constrain the displacement at each end of the plunger (the syringe, and a circular hole into which a load cell is mounted and the plunger end slides). These parts constrain displacement but do not fix the plunger’s angle at either end, so Euler’s effective-length factor $K$ is assumed to be 1 (pin-to-pin connection). Therefore, the minimum diameter is:
\begin{align*}
d &= \left( \frac{64 \times 300 \times (1 \times 0.080)^{2}}{\pi^{3} \times 2.41 \times 10^{9}} \right)^{\tfrac{1}{4}},\\
d &= 6.37~\text{mm}.
\end{align*}

As an additional safety measure, the plunger stem is specified as \SI{18}{mm}, which provides a large margin against buckling. This choice also reduces machining waste on the lathe, since the plunger head must be \SI{20}{mm} in diameter to sit within the syringe tube.

\subsubsection*{Thermal Expansion Calculations}
To allow the extruder to achieve its required maximum nozzle temperature of $85\,\,^{\circ}\text{C}$ (PR7), an E3D heater block is screwed onto the syringe's threaded nozzle and a standard 1.0 mm 3D printer nozzle is screwed into the heater block. However, the ability to elevate the syringe's temperature results in the thermal expansion of some of its components. PVC has a greater coefficient of thermal expansion than aluminium, which means that the plunger requires a minimum tolerance between the plunger head's outer diameter and syringe barrel's inner diameter must be determined to prevent the heated plunger from binding inside the syringe. According to \cite{callister2018materials}, the linear coefficients of thermal expansion for 6061 aluminium alloy and PVC are $23.6\times10^{-6}$ ($\alpha_\text{Al}$) and up to \SI{180e-6}{\per\kelvin} ($\alpha_\text{PVC}$). Therefore, the minimal diametric clearance must be (assuming $T_\text{room} = 20^{\circ}\text{C}$):
\[
\Delta d_{\text{tol}} = \left( \alpha_{\text{PVC}} - \alpha_{\text{Al}} \right) d \, \Delta T = (180-23.6)(1\times10^{-6})(20)(85-20)=\boxed{0.203~\text{mm}}.
\]
Viton O-rings are used to seal the plunger, especially when the extruder is operated at lower temperatures (increasing the clearance). Viton is selected as the O-ring material due to its high temperature resistance.

\subsubsection*{Final Design}
The final extruder design is shown below in Figure~\ref{fig:extruderFinal}.  
\begin{figure}[H]
    \centering
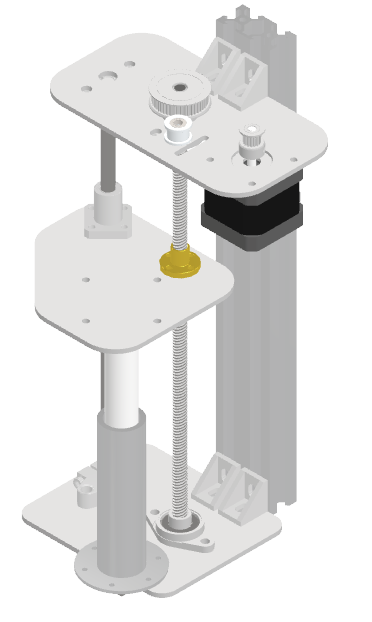
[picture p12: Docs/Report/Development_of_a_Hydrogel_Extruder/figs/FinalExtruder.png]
    
    \caption{Final Syringe-Based Extruder Design}
    \label{fig:extruderFinal}
\end{figure}
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

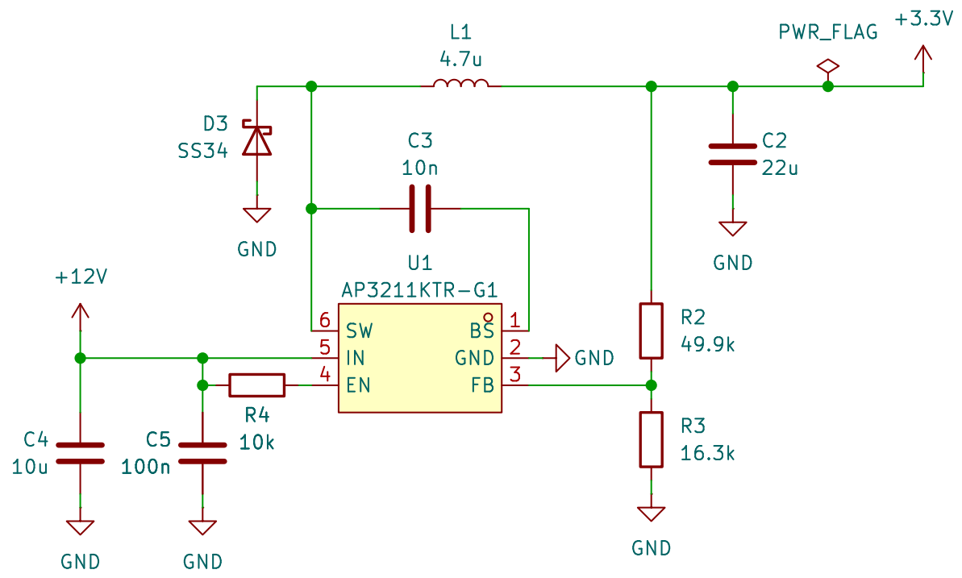
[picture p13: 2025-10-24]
Images/Electronic/PowerSchematic2.png

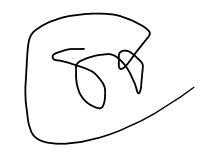
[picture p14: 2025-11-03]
Docs/Report/Development_of_a_Hydrogel_Extruder/figs/signature.png

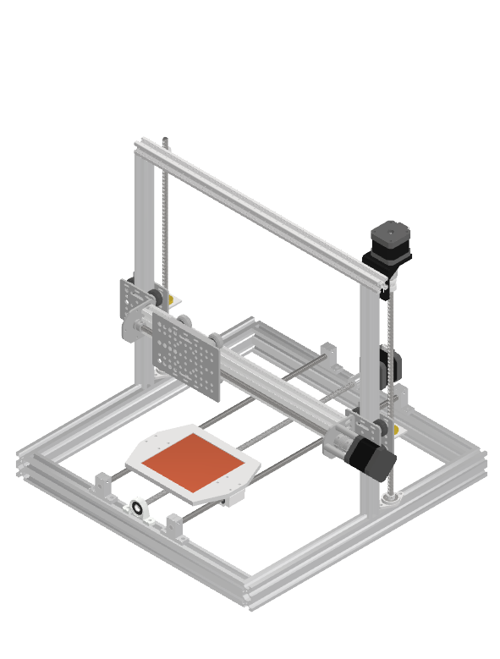
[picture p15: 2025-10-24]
Docs/Report/Development_of_a_Hydrogel_Extruder/figs/GantryConcept1.png

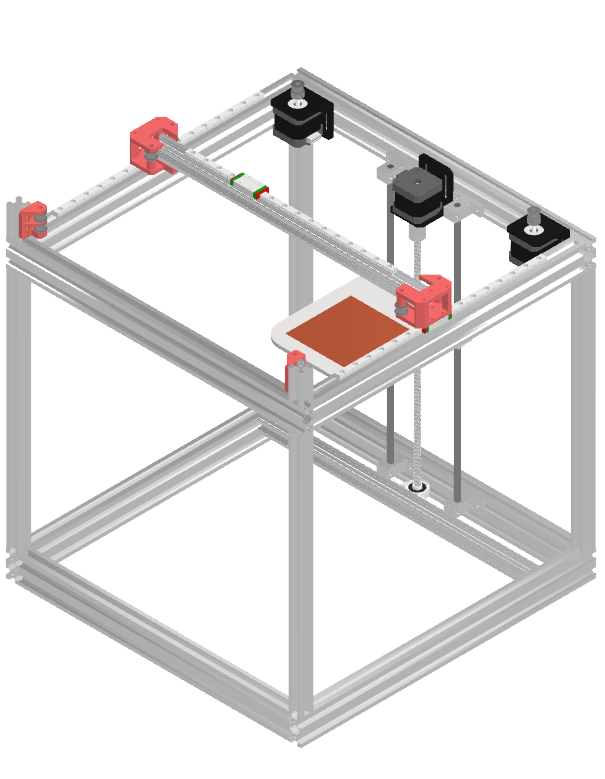
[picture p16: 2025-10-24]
Docs/Report/Development_of_a_Hydrogel_Extruder/figs/GantryConcept2.png

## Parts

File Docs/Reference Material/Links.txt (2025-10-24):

MKS Drivers:
https://github.com/makerbase-mks/MKS-StepStick-Driver/tree/master

Micro SD Reference:
https://arduino.stackexchange.com/questions/84630/proper-micro-sd-card-schematic

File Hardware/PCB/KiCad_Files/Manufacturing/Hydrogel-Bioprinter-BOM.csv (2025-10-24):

"Reference,""Qty"",""Value"",""Footprint"",""Description"",""LCSC Part"",""MANUFACTURER"""
"C2,""1"",""22u"",""Capacitor_SMD:C_0805_2012Metric"",""Unpolarized capacitor"",""C29277"",""Samsung Electro-Mechanics"""
"C3,C15,""2"",""10n"",""Capacitor_SMD:C_0603_1608Metric"",""Unpolarized capacitor"",""C1589"",""Samsung Electro-Mechanics"""
"C4,C7,C38,C41,""4"",""10u"",""Capacitor_SMD:C_0805_2012Metric"",""Unpolarized capacitor"",""C15850"",""Samsung Electro-Mechanics"""
"C5,C6,C8,C9,C10,C11,C12,C13,C14,C20,C23,C26,C27,C28,C29,C30,C36,C37,C39,C40,C42,C43,C44,C47,""24"",""100n"",""Capacitor_SMD:C_0603_1608Metric"",""Unpolarized capacitor"",""C1591"",""Samsung Electro-Mechanics"""
"C16,C17,""2"",""1u"",""Capacitor_SMD:C_0805_2012Metric"",""Unpolarized capacitor"",""C28323"",""Samsung Electro-Mechanics"""
"C18,C19,C31,C32,C33,C34,C35,C48,C49,""9"",""100u"",""Capacitor_SMD:CP_Elec_6.3x7.7"",""Polarized capacitor"",""C3339"",""Honor Elec"""
"C21,C22,""2"",""10p"",""Capacitor_SMD:C_0402_1005Metric"",""Unpolarized capacitor"",""C76945"",""muRata"""
"C24,C25,""2"",""2.2uF"",""Capacitor_SMD:C_0805_2012Metric"",""Unpolarized capacitor"",""C1731"",""Samsung Electro-Mechanics"""
"Card1,""1"",""TF-015"",""TF-SMD_TF-015:TF-SMD_TF-015"",""-35?~+85? 2mm Connector and Ejector MicroSD Card (TF Card) Push-Push SMD SD Card / Memory Card Connector ROHS"",""C113206"",""SOFNG"""
"D2,D6,D7,D8,D9,D10,D11,""7"",""SMAJ16A"",""Diode_SMD:D_SMA"",""400W unidirectional Transient Voltage Suppressor, 16.0Vr, SMA(DO-214AC)"",""C74561"",""Littelfuse"""
"D3,""1"",""SS34"",""Diode_SMD:D_SMA"",""40V 3A Schottky Diode, SMA"",""C8678"",""MDD(Microdiode Semiconductor)"""
"D4,""1"",""GREEN"",""LED_SMD:LED_0805_2012Metric"",""Light emitting diode"",""C2297"",""Hubei KENTO Elec"""
"D5,""1"",""BLUE"",""LED_SMD:LED_0805_2012Metric"",""Light emitting diode"",""C2987526"",""EVERLIGHT"""
"FB1,""1"",""120R"",""Inductor_SMD:L_0805_2012Metric"",""Ferrite bead"",""C5671"",""Sunlord"""
"J15,""1"",""USB_B_Micro"",""Connector_USB:USB_Micro-B_Molex-105017-0001"",""USB Micro Type B connector"",""C136000"",""MOLEX"""
"J16,""1"",""Conn_02x05_Odd_Even"",""Connector_PinHeader_2.54mm:PinHeader_2x05_P2.54mm_Vertical_SMD"",""Generic connector, double row, 02x05, odd/even pin numbering scheme (row 1 odd numbers, row 2 even numbers), script generated (kicad-library-utils/schlib/autogen/connector/)"",""C5160779"",""DEALON"""
"L1,""1"",""4.7u"",""Inductor_SMD:L_7.3x7.3_H4.5"",""Inductor"",""C514806"",""YJYCOIN"""
"L2,""1"",""3.3uH"",""Inductor_SMD:L_0805_2012Metric"",""Inductor"",""C162585"",""muRata"""
"Q1,""1"",""AOD4185_C400894"",""AOD4185:TO-252-3_L6.6-W6.1-P4.57-LS9.9-BR-CW"",""40V 40A 62.5W 15m?@10V 3V@250uA 1 P-Channel TO-252(DPAK) MOSFETs ROHS"",""C400894"",""AOS"""
"Q2,""1"",""MMBT4403_"",""MMBT4403_:SOT23-BEC"",""40V 100@150mA,2V 300mW 600mA PNP SOT-23 Bipolar (BJT) ROHS"",""C8513"",""JSCJ"""
"R1,R17,R25,R26,R31,R33,R38,R39,R44,R45,""10"",""100k"",""Resistor_SMD:R_0805_2012Metric"",""Resistor"",""C25611"",""UNI-ROYAL"""
"R4,R6,R9,R10,R11,R12,R13,R18,R36,R37,""10"",""10k"",""Resistor_SMD:R_0805_2012Metric"",""Resistor"",""C17414"",""UNI-ROYAL"""
"R7,R8,""2"",""4.7k"",""Resistor_SMD:R_0805_2012Metric"",""Resistor"",""C26022"",""UNI-ROYAL"""
"R14,R15,""2"",""22"",""Resistor_SMD:R_0603_1608Metric"",""Resistor"",""C1203"",""UNI-ROYAL"""
"R19,""1"",""20k"",""Resistor_SMD:R_0805_2012Metric"",""Resistor"",""C4328"",""UNI-ROYAL"""
"R20,""1"",""8.2k"",""Resistor_SMD:R_0805_2012Metric"",""Resistor"",""C17828"",""UNI-ROYAL"""
"R21,R22,""2"",""100R"",""Resistor_SMD:R_0603_1608Metric"",""Resistor"",""C22775"",""UNI-ROYAL"""
"R23,R24,R27,R29,R30,R32,R34,R35,R40,R41,R42,R43,""12"",""47R"",""Resistor_SMD:R_0805_2012Metric"",""Resistor"",""C17714"",""UNI-ROYAL"""
"SW1,""1"",""SW_SPDT"",""Button_Switch_SMD:SW_SPDT_PCM12"",""Switch, single pole double throw"",""C221841"",""C&K"""
"U1,""1"",""AP3211KTR-G1"",""AP3211KTR-G1:AP3211KTR-G1"",""Buck Adjustable 810mV~15V 1.5A 4.5V~18V SOT-23-6 DC-DC Converters ROHS"",""C154863"",""DIODES"""
"U2,""1"",""M24C64-WMN6TP"",""M24C64-WMN6TP:SOIC127P600X175-8N"",""64Kbit I2C SOIC-8 EEPROM ROHS"",""C7999"",""STMicroelectronics"""
"U3,""1"",""STM32F407VGT6"",""Package_QFP:LQFP-100_14x14mm_P0.5mm"",""STMicroelectronics Arm Cortex-M4 MCU, 1024KB flash, 192KB RAM, 168 MHz, 1.8-3.6V, 82 GPIO, LQFP100"",""C12345"",""ST"""
"U4,""1"",""HX711"",""Package_SO:SOP-16_3.9x9.9mm_P1.27mm"",""24-Bit Analog-to-Digital Converter (ADC) for Weight Scales"",""C43656"",""Avia Semicon (Xiamen)"""
"U5,""1"",""MAX6675ISA_"",""MAX6675ISA_:SOIC127P600X175-8N"",""3V~5.5V 12 SPI SOIC-8 ADCs/DACs - Special Purpose ROHS"",""C16030"",""MAXIM"""
"U6,""1"",""TMUX1208PWR"",""TMUX1208PWR:SOP65P640X120-16N"",""5? 1 8:1 TSSOP-16 Analog Switches, Multiplexers ROHS"",""C494728"",""TI"""
"U7,""1"",""SN74HC245DWR"",""SN74HC245DWR:SOIC127P1030X265-20N"",""SOIC-20-300mil Buffers, Drivers, Receivers, Transceivers ROHS"",""C10093"",""TI"""
"Y1,""1"",""16MHz"",""Crystal:Crystal_SMD_3225-4Pin_3.2x2.5mm"",""Four pin crystal, GND on pins 2 and 4"",""C112972"",""YXC Crystal Oscillators"""

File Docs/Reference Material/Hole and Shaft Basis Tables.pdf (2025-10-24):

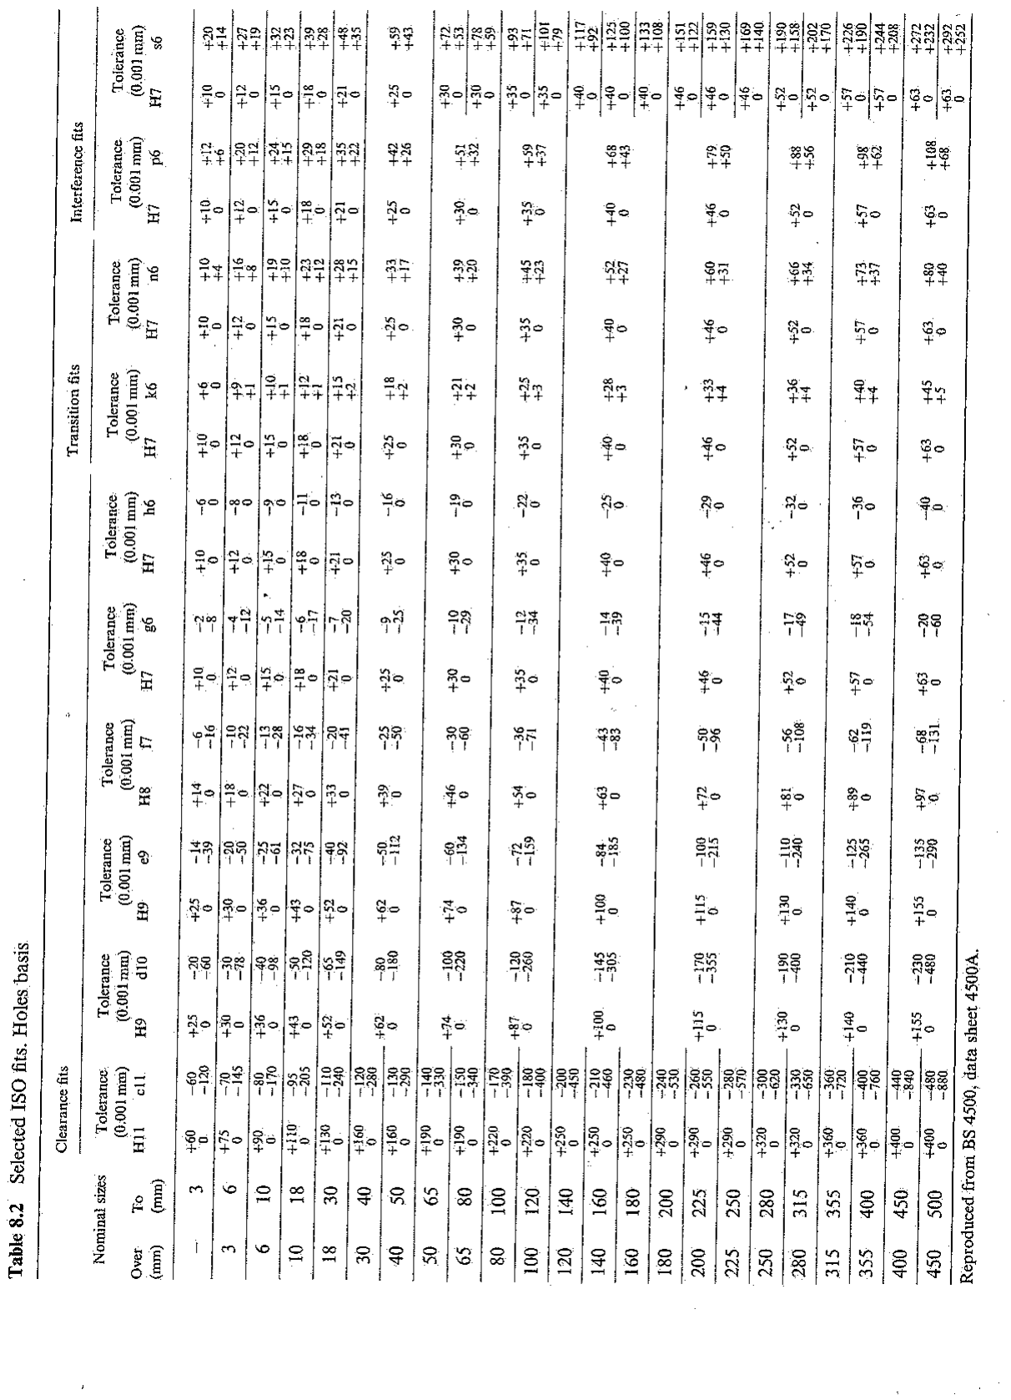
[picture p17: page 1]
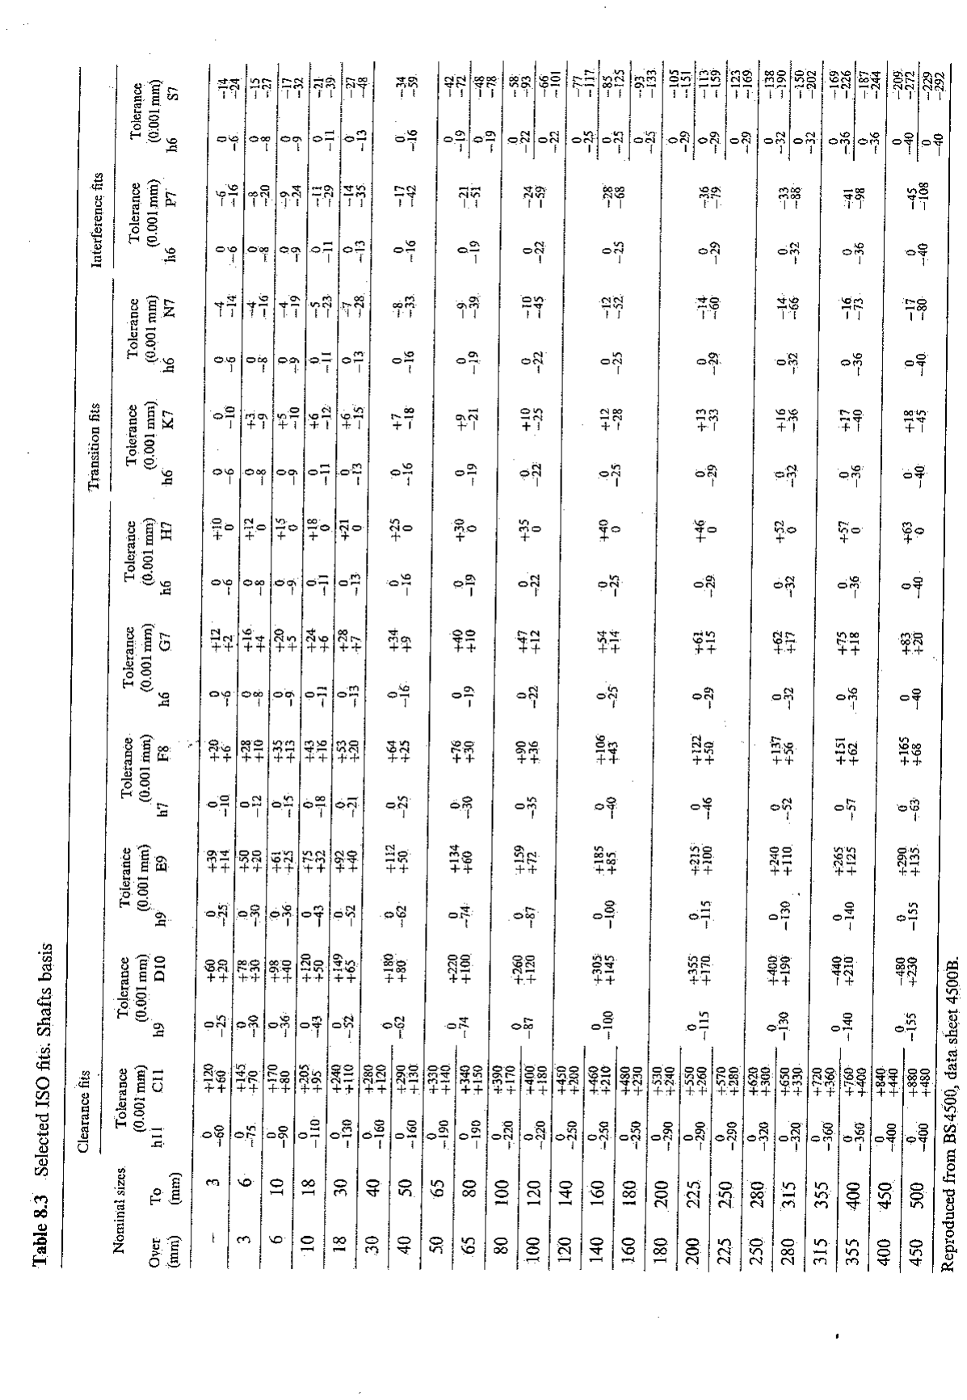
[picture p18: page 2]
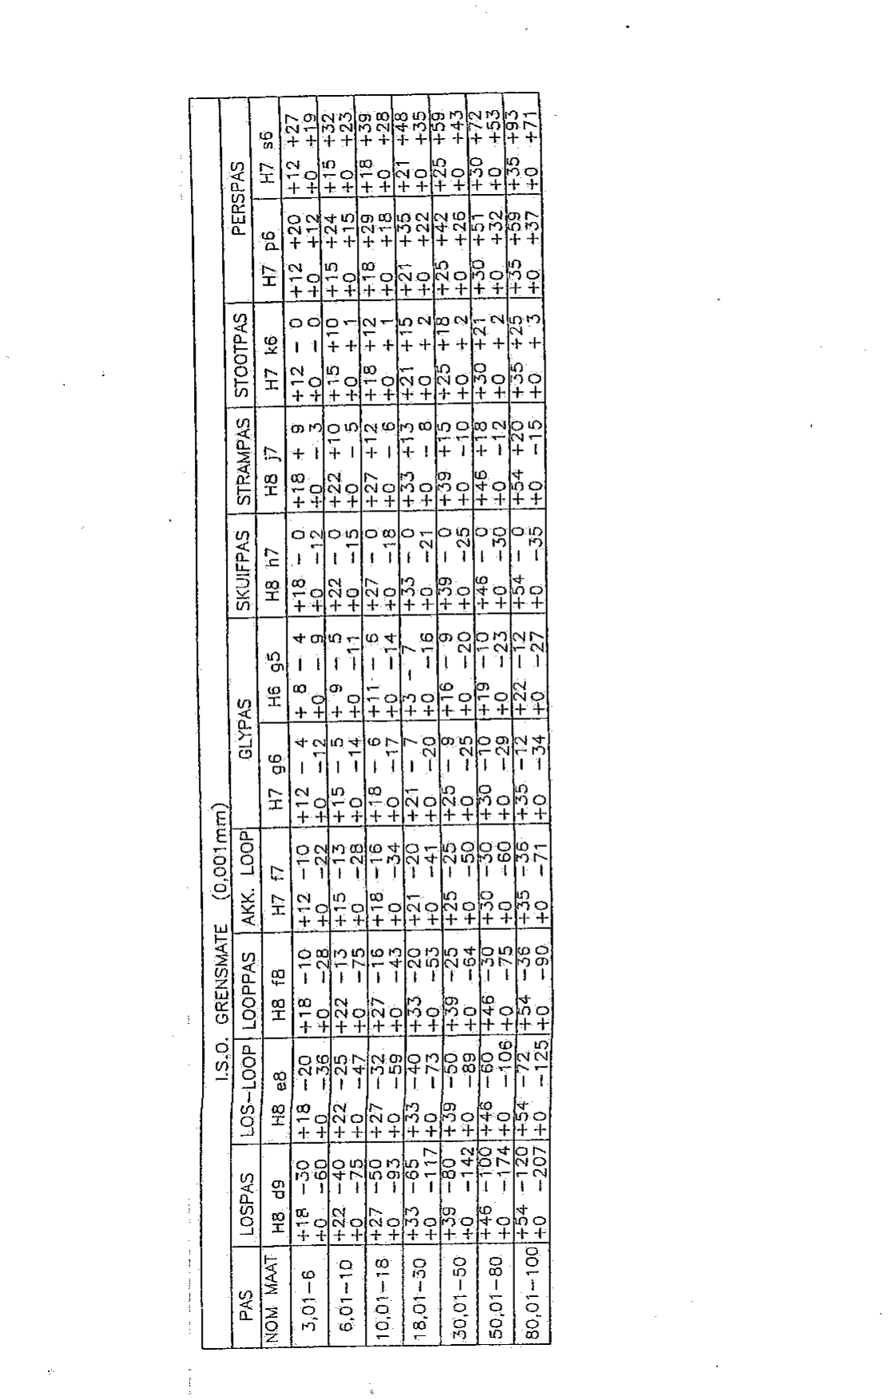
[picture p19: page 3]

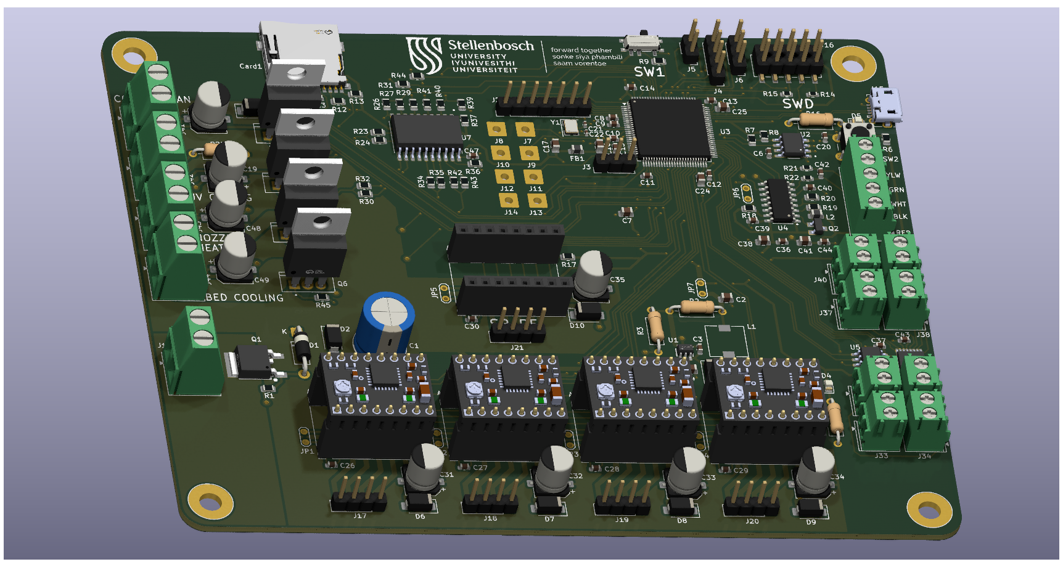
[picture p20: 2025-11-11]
Images/Video Material/HydrogelBioprinter.png

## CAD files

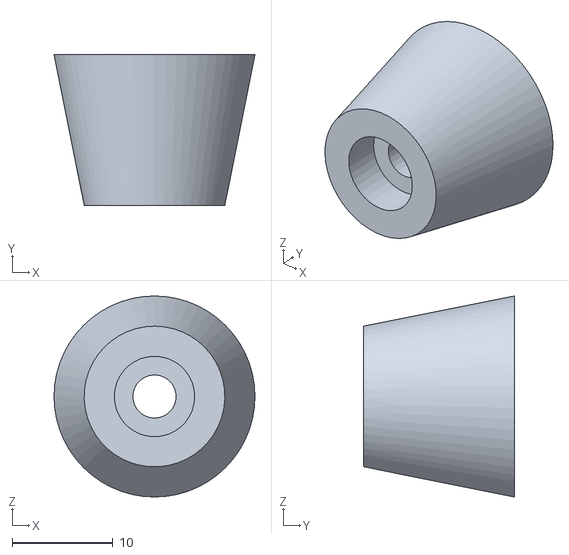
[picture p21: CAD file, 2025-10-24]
Hardware/Bioprinter Machine Design/Final System/3DPrinting/PrinterFeet.stl
20.0 x 15.0 x 20.0

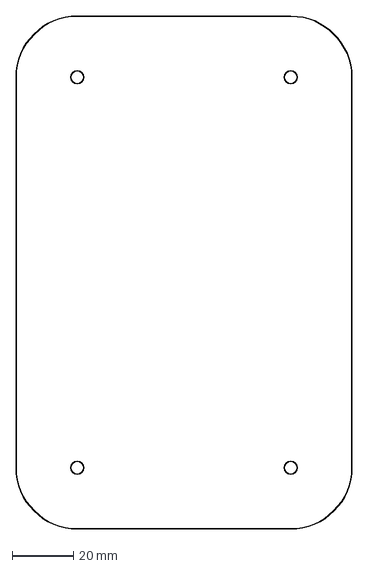
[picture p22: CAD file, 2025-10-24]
Hardware/Bioprinter Machine Design/Final System/DXFDrawingPack/ColdPlate.dxf
110.0 x 168.0 mm

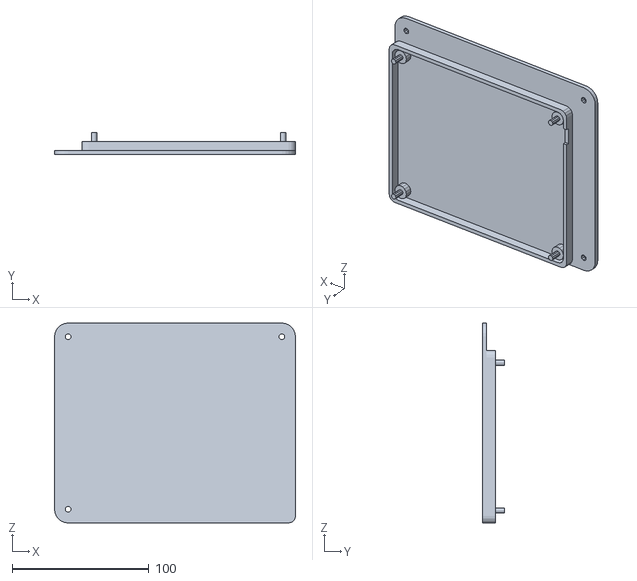
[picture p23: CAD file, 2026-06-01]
Hardware/Bioprinter Machine Design/Final System/Electronics Case/BottomCase.stl
176.0 x 16.0 x 146.0

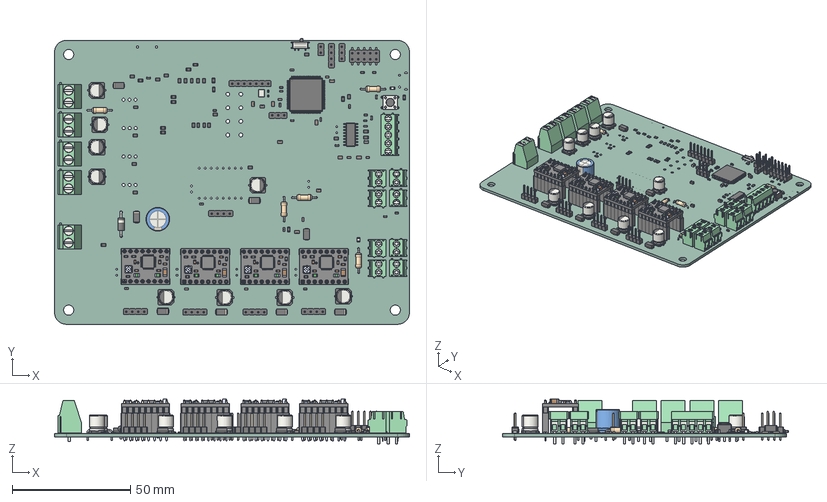
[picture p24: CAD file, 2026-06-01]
Hardware/Bioprinter Machine Design/Final System/Electronics Case/PCB/HydrogelBioprinter.step
150.0 x 120.7 x 18.9 mm
C_0603_1608Metric x 26
R_0805_2012Metric x 36
PPPC021LFBN-RC_C08 x 8
Pin - Tin x 64
A4988 STEPPER MOTOR DRIVER CARRIER--3DModel-STEP-56544 x 4
D_SMA x 8
CP_Elec_6.3x7.7 x 9
C_0805_2012Metric x 9
TerminalBlock_Phoenix_PT-1,5-2-3.5-H_1x02_P3.50mm_Horizontal x 8
PinHeader_1x07_P2.54mm_Vertical
R_Axial_DIN0207_L6.3mm_D2.5mm_P10.16mm_Horizontal x 5
TerminalBlock_Phoenix_MKDS-1,5-2-5.08_1x02_P5.08mm_Horizontal x 5
LED_0805_2012Metric x 2
CP_Radial_D10.0mm_P5.00mm
TerminalBlock_Phoenix_PT-1,5-5-3.5-H_1x05_P3.50mm_Horizontal
PinHeader_1x03_P2.54mm_Vertical x 2
PinHeader_1x04_P2.54mm_Vertical x 6
LQFP-100_14x14mm_P0.5mm
R_0603_1608Metric x 4
C_0402_1005Metric x 2
L_0805_2012Metric x 2
SW_SPDT_PCM12
SW_PUSH_6mm
D_DO-41_SOD81_P10.16mm_Horizontal
PinHeader_1x02_P2.54mm_Vertical
Crystal_SMD_3225-4Pin_3.2x2.5mm
PinHeader_2x05_P2.54mm_Vertical_SMD
SOP-16_3.9x9.9mm_P1.27mm
HydrogelBioprinter_PCB

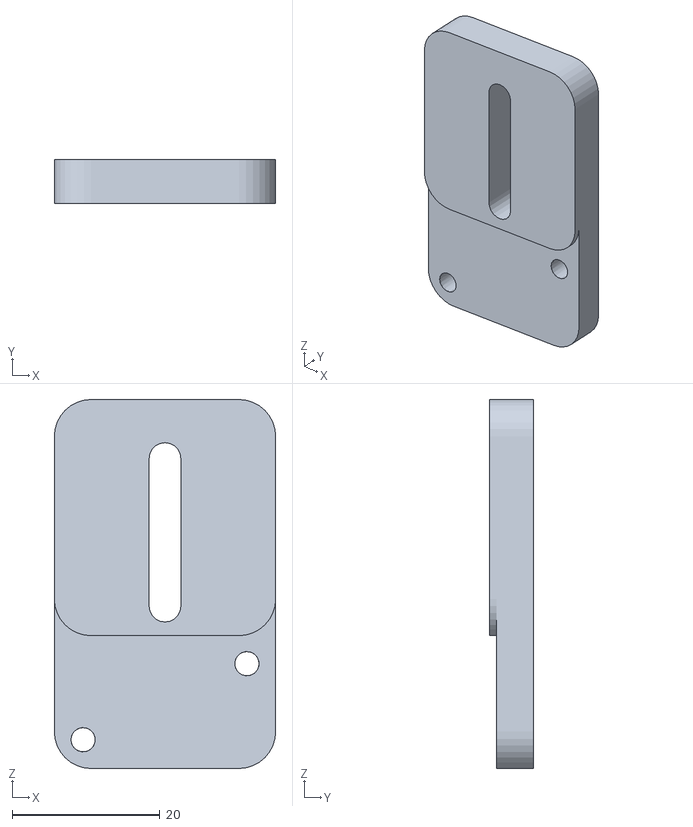
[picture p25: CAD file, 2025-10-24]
Hardware/Bioprinter Machine Design/Final System/3DPrinting/LimitSwitch.stl
30.0 x 6.00 x 50.0

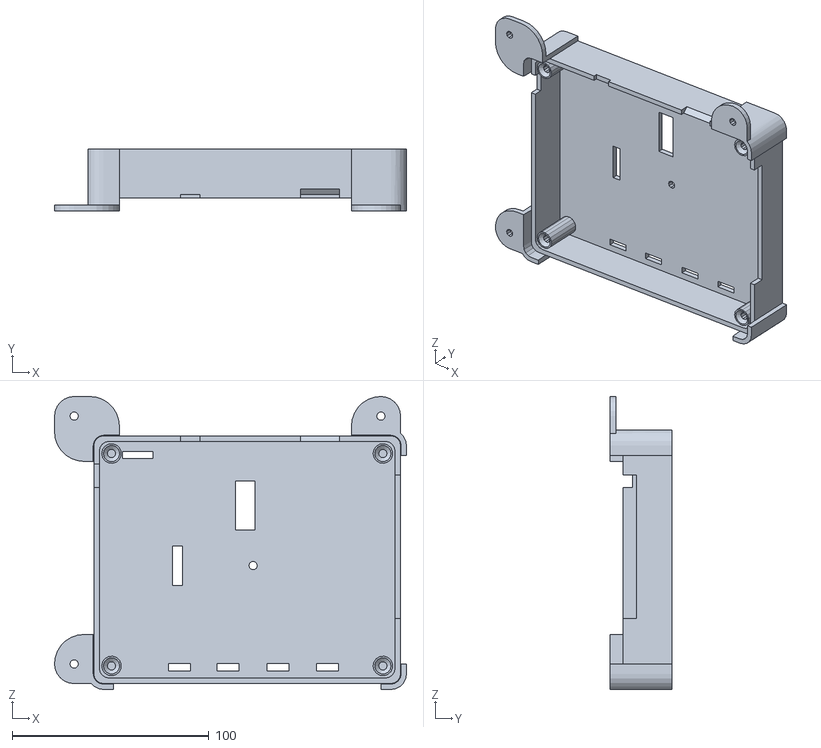
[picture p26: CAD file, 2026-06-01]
Hardware/Bioprinter Machine Design/Final System/Electronics Case/TopCase.stl
179.0 x 31.5 x 149.0

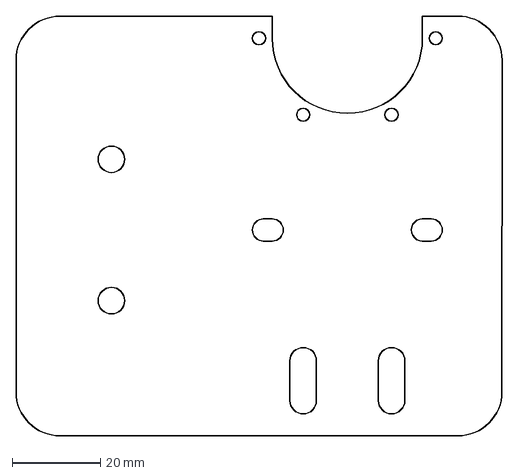
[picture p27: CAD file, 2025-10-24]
Hardware/Bioprinter Machine Design/Final System/DXFDrawingPack/BottomMount.dxf
110.0 x 95.0 mm

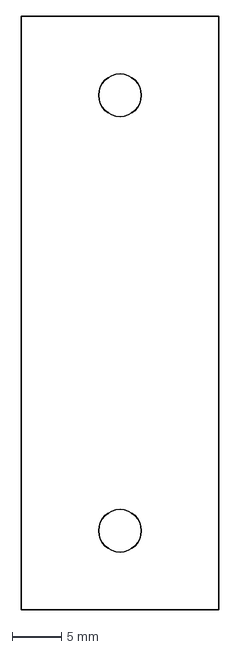
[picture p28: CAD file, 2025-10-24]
Hardware/Bioprinter Machine Design/Final System/DXFDrawingPack/BedBeltMount2.dxf
20.0 x 60.0 mm

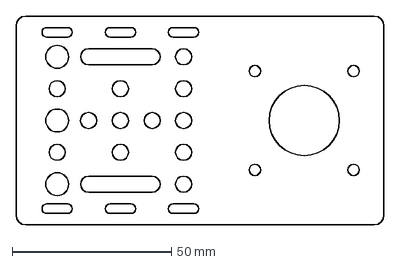
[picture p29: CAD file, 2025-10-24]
Hardware/Bioprinter Machine Design/Final System/DXFDrawingPack/CarriagePlate_Motor.dxf
115.5 x 65.5 mm

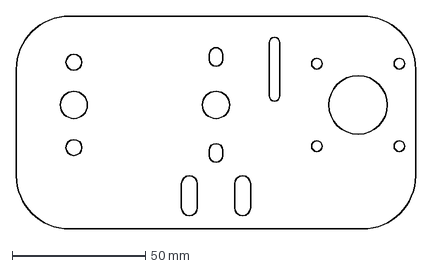
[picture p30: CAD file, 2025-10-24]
Hardware/Bioprinter Machine Design/Final System/DXFDrawingPack/TopMount.dxf
150.0 x 80.0 mm

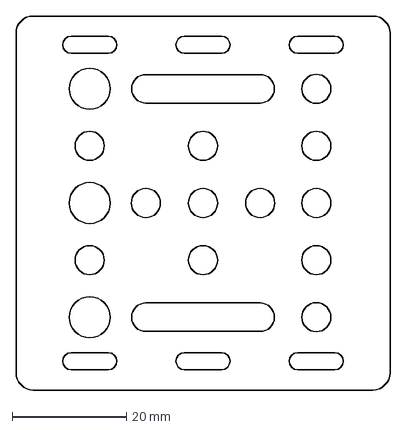
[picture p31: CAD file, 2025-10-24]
Hardware/Bioprinter Machine Design/Final System/DXFDrawingPack/CarriagePlate.dxf
65.5 x 65.5 mm

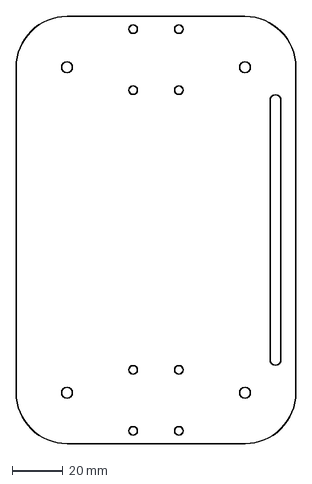
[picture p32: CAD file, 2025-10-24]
Hardware/Bioprinter Machine Design/Final System/DXFDrawingPack/BedHeatSink.dxf
110.0 x 168.0 mm

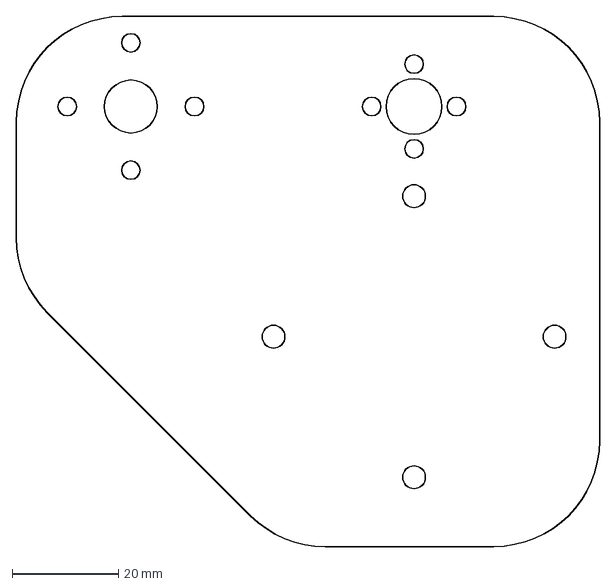
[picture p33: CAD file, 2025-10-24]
Hardware/Bioprinter Machine Design/Final System/DXFDrawingPack/MidMount.dxf
110.0 x 100.0 mm

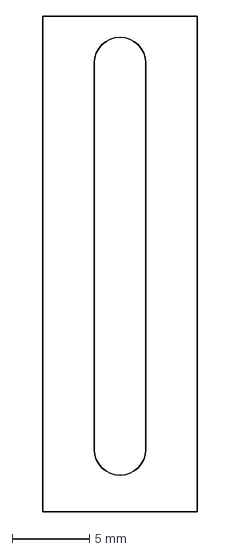
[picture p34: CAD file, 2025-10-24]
Hardware/Bioprinter Machine Design/Final System/DXFDrawingPack/BeltMount2.dxf
10.0 x 32.0 mm

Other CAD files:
Hardware/Bioprinter Machine Design/Final System/DXFDrawingPack/CarriagePlate_Idler.dxf
Hardware/Bioprinter Machine Design/Final System/DXFDrawingPack/LeadScrewEndMount.dxf
Hardware/Bioprinter Machine Design/Extruder Concept 1/ExtruderFrame.ipt
Hardware/Bioprinter Machine Design/Extruder Concept 1/OldVersions/ExtruderFrame.0007.ipt
Hardware/Bioprinter Machine Design/Extruder Concept 1/OldVersions/SpurGearPrimary.0002.ipt
Hardware/Bioprinter Machine Design/Extruder Concept 1/OldVersions/SpurGearSecondary.0003.ipt
Hardware/Bioprinter Machine Design/Extruder Concept 1/OldVersions/SyringeConcept1.0009.iam
Hardware/Bioprinter Machine Design/Extruder Concept 1/OldVersions/SyringeHolder.0001.ipt
Hardware/Bioprinter Machine Design/Extruder Concept 1/OldVersions/SyringePushMount.0007.ipt
Hardware/Bioprinter Machine Design/Extruder Concept 1/OldVersions/TR8x8-4_LeadScrew.0001.ipt
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

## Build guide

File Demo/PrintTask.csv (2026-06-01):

X | Y | Z | Speed | E | Mode | NozzleTemp
210.000 | 270.000 | -90.000 | 40.000 | 0.00000 | 0 | 45.0
210.000 | 270.000 | -90.000 | 2.000 | 10.00000 | 0 | 45.0
135.000 | 190.500 | -98.500 | 20.000 | 10.00000 | 0 | 45.0
0.000 | 0.000 | 13.500 | 20.000 | 0.00000 | 1 | 50.0
0.000 | -30.000 | 0.000 | 20.000 | 0.00000 | 1 | 50.0
0.000 | 0.000 | -9.500 | 20.000 | 0.00000 | 1 | 50.0
2.615 | 0.114 | 0.000 | 10.000 | 0.10469 | 1 | 50.0
2.595 | 0.342 | 0.000 | 10.000 | 0.10469 | 1 | 50.0
2.555 | 0.566 | 0.000 | 10.000 | 0.10469 | 1 | 50.0
2.496 | 0.787 | 0.000 | 10.000 | 0.10469 | 1 | 50.0
2.418 | 1.002 | 0.000 | 10.000 | 0.10469 | 1 | 50.0
2.321 | 1.208 | 0.000 | 10.000 | 0.10469 | 1 | 50.0
2.207 | 1.406 | 0.000 | 10.000 | 0.10469 | 1 | 50.0
2.076 | 1.593 | 0.000 | 10.000 | 0.10469 | 1 | 50.0
1.930 | 1.768 | 0.000 | 10.000 | 0.10469 | 1 | 50.0
1.768 | 1.930 | 0.000 | 10.000 | 0.10469 | 1 | 50.0
1.593 | 2.076 | 0.000 | 10.000 | 0.10469 | 1 | 50.0
1.406 | 2.207 | 0.000 | 10.000 | 0.10469 | 1 | 50.0
1.208 | 2.321 | 0.000 | 10.000 | 0.10469 | 1 | 50.0
1.002 | 2.418 | 0.000 | 10.000 | 0.10469 | 1 | 50.0
0.787 | 2.496 | 0.000 | 10.000 | 0.10469 | 1 | 50.0
0.566 | 2.555 | 0.000 | 10.000 | 0.10469 | 1 | 50.0
0.342 | 2.595 | 0.000 | 10.000 | 0.10469 | 1 | 50.0
0.114 | 2.615 | 0.000 | 10.000 | 0.10469 | 1 | 50.0
-0.114 | 2.615 | 0.000 | 10.000 | 0.10469 | 1 | 50.0
-0.342 | 2.595 | 0.000 | 10.000 | 0.10469 | 1 | 50.0
-0.566 | 2.555 | 0.000 | 10.000 | 0.10469 | 1 | 50.0
-0.787 | 2.496 | 0.000 | 10.000 | 0.10469 | 1 | 50.0
-1.002 | 2.418 | 0.000 | 10.000 | 0.10469 | 1 | 50.0
-1.208 | 2.321 | 0.000 | 10.000 | 0.10469 | 1 | 50.0
-1.406 | 2.207 | 0.000 | 10.000 | 0.10469 | 1 | 50.0
-1.593 | 2.076 | 0.000 | 10.000 | 0.10469 | 1 | 50.0
-1.768 | 1.930 | 0.000 | 10.000 | 0.10469 | 1 | 50.0
-1.930 | 1.768 | 0.000 | 10.000 | 0.10469 | 1 | 50.0
-2.076 | 1.593 | 0.000 | 10.000 | 0.10469 | 1 | 50.0
-2.207 | 1.406 | 0.000 | 10.000 | 0.10469 | 1 | 50.0
-2.321 | 1.208 | 0.000 | 10.000 | 0.10469 | 1 | 50.0
-2.418 | 1.002 | 0.000 | 10.000 | 0.10469 | 1 | 50.0
-2.496 | 0.787 | 0.000 | 10.000 | 0.10469 | 1 | 50.0
-2.555 | 0.566 | 0.000 | 10.000 | 0.10469 | 1 | 50.0
-2.595 | 0.342 | 0.000 | 10.000 | 0.10469 | 1 | 50.0
-2.615 | 0.114 | 0.000 | 10.000 | 0.10469 | 1 | 50.0
-2.615 | -0.114 | 0.000 | 10.000 | 0.10469 | 1 | 50.0
-2.595 | -0.342 | 0.000 | 10.000 | 0.10469 | 1 | 50.0
-2.555 | -0.566 | 0.000 | 10.000 | 0.10469 | 1 | 50.0
-2.496 | -0.787 | 0.000 | 10.000 | 0.10469 | 1 | 50.0
-2.418 | -1.002 | 0.000 | 10.000 | 0.10469 | 1 | 50.0
-2.321 | -1.208 | 0.000 | 10.000 | 0.10469 | 1 | 50.0
-2.207 | -1.406 | 0.000 | 10.000 | 0.10469 | 1 | 50.0
-2.076 | -1.593 | 0.000 | 10.000 | 0.10469 | 1 | 50.0
-1.930 | -1.768 | 0.000 | 10.000 | 0.10469 | 1 | 50.0
-1.768 | -1.930 | 0.000 | 10.000 | 0.10469 | 1 | 50.0
-1.593 | -2.076 | 0.000 | 10.000 | 0.10469 | 1 | 50.0
-1.406 | -2.207 | 0.000 | 10.000 | 0.10469 | 1 | 50.0
-1.208 | -2.321 | 0.000 | 10.000 | 0.10469 | 1 | 50.0
-1.002 | -2.418 | 0.000 | 10.000 | 0.10469 | 1 | 50.0
-0.787 | -2.496 | 0.000 | 10.000 | 0.10469 | 1 | 50.0
-0.566 | -2.555 | 0.000 | 10.000 | 0.10469 | 1 | 50.0
-0.342 | -2.595 | 0.000 | 10.000 | 0.10469 | 1 | 50.0
-0.114 | -2.615 | 0.000 | 10.000 | 0.10469 | 1 | 50.0
0.114 | -2.615 | 0.000 | 10.000 | 0.10469 | 1 | 50.0
0.342 | -2.595 | 0.000 | 10.000 | 0.10469 | 1 | 50.0
0.566 | -2.555 | 0.000 | 10.000 | 0.10469 | 1 | 50.0
0.787 | -2.496 | 0.000 | 10.000 | 0.10469 | 1 | 50.0
1.002 | -2.418 | 0.000 | 10.000 | 0.10469 | 1 | 50.0
1.208 | -2.321 | 0.000 | 10.000 | 0.10469 | 1 | 50.0
1.406 | -2.207 | 0.000 | 10.000 | 0.10469 | 1 | 50.0
1.593 | -2.076 | 0.000 | 10.000 | 0.10469 | 1 | 50.0
1.768 | -1.930 | 0.000 | 10.000 | 0.10469 | 1 | 50.0
1.930 | -1.768 | 0.000 | 10.000 | 0.10469 | 1 | 50.0
2.076 | -1.593 | 0.000 | 10.000 | 0.10469 | 1 | 50.0
2.207 | -1.406 | 0.000 | 10.000 | 0.10469 | 1 | 50.0
2.321 | -1.208 | 0.000 | 10.000 | 0.10469 | 1 | 50.0
2.418 | -1.002 | 0.000 | 10.000 | 0.10469 | 1 | 50.0
2.496 | -0.787 | 0.000 | 10.000 | 0.10469 | 1 | 50.0
2.555 | -0.566 | 0.000 | 10.000 | 0.10469 | 1 | 50.0
2.595 | -0.342 | 0.000 | 10.000 | 0.10469 | 1 | 50.0
2.615 | -0.114 | 0.000 | 10.000 | 0.10469 | 1 | 50.0
0.000 | 0.000 | 3.000 | 20.000 | 0.00000 | 1 | 50.0
2.615 | 0.114 | 0.000 | 10.000 | 0.10469 | 1 | 50.0
2.595 | 0.342 | 0.000 | 10.000 | 0.10469 | 1 | 50.0
2.555 | 0.566 | 0.000 | 10.000 | 0.10469 | 1 | 50.0
2.496 | 0.787 | 0.000 | 10.000 | 0.10469 | 1 | 50.0
2.418 | 1.002 | 0.000 | 10.000 | 0.10469 | 1 | 50.0
2.321 | 1.208 | 0.000 | 10.000 | 0.10469 | 1 | 50.0
2.207 | 1.406 | 0.000 | 10.000 | 0.10469 | 1 | 50.0
2.076 | 1.593 | 0.000 | 10.000 | 0.10469 | 1 | 50.0
1.930 | 1.768 | 0.000 | 10.000 | 0.10469 | 1 | 50.0
1.768 | 1.930 | 0.000 | 10.000 | 0.10469 | 1 | 50.0
1.593 | 2.076 | 0.000 | 10.000 | 0.10469 | 1 | 50.0
1.406 | 2.207 | 0.000 | 10.000 | 0.10469 | 1 | 50.0
1.208 | 2.321 | 0.000 | 10.000 | 0.10469 | 1 | 50.0
1.002 | 2.418 | 0.000 | 10.000 | 0.10469 | 1 | 50.0
0.787 | 2.496 | 0.000 | 10.000 | 0.10469 | 1 | 50.0
0.566 | 2.555 | 0.000 | 10.000 | 0.10469 | 1 | 50.0
0.342 | 2.595 | 0.000 | 10.000 | 0.10469 | 1 | 50.0
0.114 | 2.615 | 0.000 | 10.000 | 0.10469 | 1 | 50.0
-0.114 | 2.615 | 0.000 | 10.000 | 0.10469 | 1 | 50.0
-0.342 | 2.595 | 0.000 | 10.000 | 0.10469 | 1 | 50.0
-0.566 | 2.555 | 0.000 | 10.000 | 0.10469 | 1 | 50.0
-0.787 | 2.496 | 0.000 | 10.000 | 0.10469 | 1 | 50.0
-1.002 | 2.418 | 0.000 | 10.000 | 0.10469 | 1 | 50.0
-1.208 | 2.321 | 0.000 | 10.000 | 0.10469 | 1 | 50.0
-1.406 | 2.207 | 0.000 | 10.000 | 0.10469 | 1 | 50.0
-1.593 | 2.076 | 0.000 | 10.000 | 0.10469 | 1 | 50.0
-1.768 | 1.930 | 0.000 | 10.000 | 0.10469 | 1 | 50.0
-1.930 | 1.768 | 0.000 | 10.000 | 0.10469 | 1 | 50.0
-2.076 | 1.593 | 0.000 | 10.000 | 0.10469 | 1 | 50.0
-2.207 | 1.406 | 0.000 | 10.000 | 0.10469 | 1 | 50.0
-2.321 | 1.208 | 0.000 | 10.000 | 0.10469 | 1 | 50.0
-2.418 | 1.002 | 0.000 | 10.000 | 0.10469 | 1 | 50.0
-2.496 | 0.787 | 0.000 | 10.000 | 0.10469 | 1 | 50.0
-2.555 | 0.566 | 0.000 | 10.000 | 0.10469 | 1 | 50.0
-2.595 | 0.342 | 0.000 | 10.000 | 0.10469 | 1 | 50.0
-2.615 | 0.114 | 0.000 | 10.000 | 0.10469 | 1 | 50.0
-2.615 | -0.114 | 0.000 | 10.000 | 0.10469 | 1 | 50.0
-2.595 | -0.342 | 0.000 | 10.000 | 0.10469 | 1 | 50.0
-2.555 | -0.566 | 0.000 | 10.000 | 0.10469 | 1 | 50.0
-2.496 | -0.787 | 0.000 | 10.000 | 0.10469 | 1 | 50.0
-2.418 | -1.002 | 0.000 | 10.000 | 0.10469 | 1 | 50.0
-2.321 | -1.208 | 0.000 | 10.000 | 0.10469 | 1 | 50.0
-2.207 | -1.406 | 0.000 | 10.000 | 0.10469 | 1 | 50.0
-2.076 | -1.593 | 0.000 | 10.000 | 0.10469 | 1 | 50.0
-1.930 | -1.768 | 0.000 | 10.000 | 0.10469 | 1 | 50.0
-1.768 | -1.930 | 0.000 | 10.000 | 0.10469 | 1 | 50.0
-1.593 | -2.076 | 0.000 | 10.000 | 0.10469 | 1 | 50.0
-1.406 | -2.207 | 0.000 | 10.000 | 0.10469 | 1 | 50.0
-1.208 | -2.321 | 0.000 | 10.000 | 0.10469 | 1 | 50.0
-1.002 | -2.418 | 0.000 | 10.000 | 0.10469 | 1 | 50.0
-0.787 | -2.496 | 0.000 | 10.000 | 0.10469 | 1 | 50.0
-0.566 | -2.555 | 0.000 | 10.000 | 0.10469 | 1 | 50.0
-0.342 | -2.595 | 0.000 | 10.000 | 0.10469 | 1 | 50.0
-0.114 | -2.615 | 0.000 | 10.000 | 0.10469 | 1 | 50.0
0.114 | -2.615 | 0.000 | 10.000 | 0.10469 | 1 | 50.0
0.342 | -2.595 | 0.000 | 10.000 | 0.10469 | 1 | 50.0
0.566 | -2.555 | 0.000 | 10.000 | 0.10469 | 1 | 50.0
0.787 | -2.496 | 0.000 | 10.000 | 0.10469 | 1 | 50.0
1.002 | -2.418 | 0.000 | 10.000 | 0.10469 | 1 | 50.0
1.208 | -2.321 | 0.000 | 10.000 | 0.10469 | 1 | 50.0
1.406 | -2.207 | 0.000 | 10.000 | 0.10469 | 1 | 50.0
1.593 | -2.076 | 0.000 | 10.000 | 0.10469 | 1 | 50.0
1.768 | -1.930 | 0.000 | 10.000 | 0.10469 | 1 | 50.0
1.930 | -1.768 | 0.000 | 10.000 | 0.10469 | 1 | 50.0
2.076 | -1.593 | 0.000 | 10.000 | 0.10469 | 1 | 50.0
2.207 | -1.406 | 0.000 | 10.000 | 0.10469 | 1 | 50.0
2.321 | -1.208 | 0.000 | 10.000 | 0.10469 | 1 | 50.0
2.418 | -1.002 | 0.000 | 10.000 | 0.10469 | 1 | 50.0
2.496 | -0.787 | 0.000 | 10.000 | 0.10469 | 1 | 50.0
2.555 | -0.566 | 0.000 | 10.000 | 0.10469 | 1 | 50.0
2.595 | -0.342 | 0.000 | 10.000 | 0.10469 | 1 | 50.0
2.615 | -0.114 | 0.000 | 10.000 | 0.10469 | 1 | 50.0
0.000 | 0.000 | 3.000 | 20.000 | 0.00000 | 1 | 50.0
2.615 | 0.114 | 0.000 | 10.000 | 0.10469 | 1 | 50.0
2.595 | 0.342 | 0.000 | 10.000 | 0.10469 | 1 | 50.0
2.555 | 0.566 | 0.000 | 10.000 | 0.10469 | 1 | 50.0
2.496 | 0.787 | 0.000 | 10.000 | 0.10469 | 1 | 50.0
2.418 | 1.002 | 0.000 | 10.000 | 0.10469 | 1 | 50.0
2.321 | 1.208 | 0.000 | 10.000 | 0.10469 | 1 | 50.0
2.207 | 1.406 | 0.000 | 10.000 | 0.10469 | 1 | 50.0
2.076 | 1.593 | 0.000 | 10.000 | 0.10469 | 1 | 50.0
1.930 | 1.768 | 0.000 | 10.000 | 0.10469 | 1 | 50.0
1.768 | 1.930 | 0.000 | 10.000 | 0.10469 | 1 | 50.0
1.593 | 2.076 | 0.000 | 10.000 | 0.10469 | 1 | 50.0
1.406 | 2.207 | 0.000 | 10.000 | 0.10469 | 1 | 50.0
1.208 | 2.321 | 0.000 | 10.000 | 0.10469 | 1 | 50.0
1.002 | 2.418 | 0.000 | 10.000 | 0.10469 | 1 | 50.0
0.787 | 2.496 | 0.000 | 10.000 | 0.10469 | 1 | 50.0
0.566 | 2.555 | 0.000 | 10.000 | 0.10469 | 1 | 50.0
0.342 | 2.595 | 0.000 | 10.000 | 0.10469 | 1 | 50.0
0.114 | 2.615 | 0.000 | 10.000 | 0.10469 | 1 | 50.0
-0.114 | 2.615 | 0.000 | 10.000 | 0.10469 | 1 | 50.0
-0.342 | 2.595 | 0.000 | 10.000 | 0.10469 | 1 | 50.0
-0.566 | 2.555 | 0.000 | 10.000 | 0.10469 | 1 | 50.0
-0.787 | 2.496 | 0.000 | 10.000 | 0.10469 | 1 | 50.0
-1.002 | 2.418 | 0.000 | 10.000 | 0.10469 | 1 | 50.0
-1.208 | 2.321 | 0.000 | 10.000 | 0.10469 | 1 | 50.0
-1.406 | 2.207 | 0.000 | 10.000 | 0.10469 | 1 | 50.0
-1.593 | 2.076 | 0.000 | 10.000 | 0.10469 | 1 | 50.0
-1.768 | 1.930 | 0.000 | 10.000 | 0.10469 | 1 | 50.0
-1.930 | 1.768 | 0.000 | 10.000 | 0.10469 | 1 | 50.0
-2.076 | 1.593 | 0.000 | 10.000 | 0.10469 | 1 | 50.0
-2.207 | 1.406 | 0.000 | 10.000 | 0.10469 | 1 | 50.0
-2.321 | 1.208 | 0.000 | 10.000 | 0.10469 | 1 | 50.0
-2.418 | 1.002 | 0.000 | 10.000 | 0.10469 | 1 | 50.0
-2.496 | 0.787 | 0.000 | 10.000 | 0.10469 | 1 | 50.0
-2.555 | 0.566 | 0.000 | 10.000 | 0.10469 | 1 | 50.0
-2.595 | 0.342 | 0.000 | 10.000 | 0.10469 | 1 | 50.0
-2.615 | 0.114 | 0.000 | 10.000 | 0.10469 | 1 | 50.0
-2.615 | -0.114 | 0.000 | 10.000 | 0.10469 | 1 | 50.0
-2.595 | -0.342 | 0.000 | 10.000 | 0.10469 | 1 | 50.0
-2.555 | -0.566 | 0.000 | 10.000 | 0.10469 | 1 | 50.0
-2.496 | -0.787 | 0.000 | 10.000 | 0.10469 | 1 | 50.0
-2.418 | -1.002 | 0.000 | 10.000 | 0.10469 | 1 | 50.0
-2.321 | -1.208 | 0.000 | 10.000 | 0.10469 | 1 | 50.0
-2.207 | -1.406 | 0.000 | 10.000 | 0.10469 | 1 | 50.0
-2.076 | -1.593 | 0.000 | 10.000 | 0.10469 | 1 | 50.0
-1.930 | -1.768 | 0.000 | 10.000 | 0.10469 | 1 | 50.0
-1.768 | -1.930 | 0.000 | 10.000 | 0.10469 | 1 | 50.0
-1.593 | -2.076 | 0.000 | 10.000 | 0.10469 | 1 | 50.0
-1.406 | -2.207 | 0.000 | 10.000 | 0.10469 | 1 | 50.0
-1.208 | -2.321 | 0.000 | 10.000 | 0.10469 | 1 | 50.0
-1.002 | -2.418 | 0.000 | 10.000 | 0.10469 | 1 | 50.0
-0.787 | -2.496 | 0.000 | 10.000 | 0.10469 | 1 | 50.0
-0.566 | -2.555 | 0.000 | 10.000 | 0.10469 | 1 | 50.0
-0.342 | -2.595 | 0.000 | 10.000 | 0.10469 | 1 | 50.0
-0.114 | -2.615 | 0.000 | 10.000 | 0.10469 | 1 | 50.0
0.114 | -2.615 | 0.000 | 10.000 | 0.10469 | 1 | 50.0
0.342 | -2.595 | 0.000 | 10.000 | 0.10469 | 1 | 50.0
0.566 | -2.555 | 0.000 | 10.000 | 0.10469 | 1 | 50.0
0.787 | -2.496 | 0.000 | 10.000 | 0.10469 | 1 | 50.0
1.002 | -2.418 | 0.000 | 10.000 | 0.10469 | 1 | 50.0
1.208 | -2.321 | 0.000 | 10.000 | 0.10469 | 1 | 50.0
1.406 | -2.207 | 0.000 | 10.000 | 0.10469 | 1 | 50.0
1.593 | -2.076 | 0.000 | 10.000 | 0.10469 | 1 | 50.0
1.768 | -1.930 | 0.000 | 10.000 | 0.10469 | 1 | 50.0
1.930 | -1.768 | 0.000 | 10.000 | 0.10469 | 1 | 50.0
2.076 | -1.593 | 0.000 | 10.000 | 0.10469 | 1 | 50.0
2.207 | -1.406 | 0.000 | 10.000 | 0.10469 | 1 | 50.0
2.321 | -1.208 | 0.000 | 10.000 | 0.10469 | 1 | 50.0
2.418 | -1.002 | 0.000 | 10.000 | 0.10469 | 1 | 50.0
2.496 | -0.787 | 0.000 | 10.000 | 0.10469 | 1 | 50.0
2.555 | -0.566 | 0.000 | 10.000 | 0.10469 | 1 | 50.0
2.595 | -0.342 | 0.000 | 10.000 | 0.10469 | 1 | 50.0
2.615 | -0.114 | 0.000 | 10.000 | 0.10469 | 1 | 50.0
0.000 | 0.000 | 3.500 | 20.000 | 0.00000 | 1 | 50.0
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

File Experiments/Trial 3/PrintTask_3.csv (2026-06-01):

X | Y | Z | Speed | E | Mode | NozzleTemp
210.000 | 270.000 | -90.000 | 40.000 | 0.00000 | 0 | 45.0
210.000 | 270.000 | -90.000 | 2.000 | 10.00000 | 0 | 45.0
135.000 | 170.500 | -98.800 | 20.000 | 10.00000 | 0 | 45.0
0.000 | 0.000 | 3.800 | 20.000 | 0.00000 | 1 | 50.0
0.000 | -5.000 | 0.000 | 20.000 | 0.00000 | 1 | 50.0
0.000 | 0.000 | -3.800 | 20.000 | 0.00000 | 1 | 50.0
0.174 | 0.003 | 0.000 | 20.000 | 0.00349 | 1 | 50.0
0.174 | 0.009 | 0.000 | 20.000 | 0.00349 | 1 | 50.0
0.174 | 0.015 | 0.000 | 20.000 | 0.00349 | 1 | 50.0
0.173 | 0.021 | 0.000 | 20.000 | 0.00349 | 1 | 50.0
0.172 | 0.027 | 0.000 | 20.000 | 0.00349 | 1 | 50.0
0.171 | 0.033 | 0.000 | 20.000 | 0.00349 | 1 | 50.0
0.170 | 0.039 | 0.000 | 20.000 | 0.00349 | 1 | 50.0
0.169 | 0.045 | 0.000 | 20.000 | 0.00349 | 1 | 50.0
0.167 | 0.051 | 0.000 | 20.000 | 0.00349 | 1 | 50.0
0.165 | 0.057 | 0.000 | 20.000 | 0.00349 | 1 | 50.0
0.163 | 0.063 | 0.000 | 20.000 | 0.00349 | 1 | 50.0
0.161 | 0.068 | 0.000 | 20.000 | 0.00349 | 1 | 50.0
0.158 | 0.074 | 0.000 | 20.000 | 0.00349 | 1 | 50.0
0.156 | 0.079 | 0.000 | 20.000 | 0.00349 | 1 | 50.0
0.153 | 0.085 | 0.000 | 20.000 | 0.00349 | 1 | 50.0
0.150 | 0.090 | 0.000 | 20.000 | 0.00349 | 1 | 50.0
0.146 | 0.095 | 0.000 | 20.000 | 0.00349 | 1 | 50.0
0.143 | 0.100 | 0.000 | 20.000 | 0.00349 | 1 | 50.0
0.139 | 0.105 | 0.000 | 20.000 | 0.00349 | 1 | 50.0
0.136 | 0.110 | 0.000 | 20.000 | 0.00349 | 1 | 50.0
0.132 | 0.114 | 0.000 | 20.000 | 0.00349 | 1 | 50.0
0.128 | 0.119 | 0.000 | 20.000 | 0.00349 | 1 | 50.0
0.123 | 0.123 | 0.000 | 20.000 | 0.00349 | 1 | 50.0
0.119 | 0.128 | 0.000 | 20.000 | 0.00349 | 1 | 50.0
0.114 | 0.132 | 0.000 | 20.000 | 0.00349 | 1 | 50.0
0.110 | 0.136 | 0.000 | 20.000 | 0.00349 | 1 | 50.0
0.105 | 0.139 | 0.000 | 20.000 | 0.00349 | 1 | 50.0
0.100 | 0.143 | 0.000 | 20.000 | 0.00349 | 1 | 50.0
0.095 | 0.146 | 0.000 | 20.000 | 0.00349 | 1 | 50.0
0.090 | 0.150 | 0.000 | 20.000 | 0.00349 | 1 | 50.0
0.085 | 0.153 | 0.000 | 20.000 | 0.00349 | 1 | 50.0
0.079 | 0.156 | 0.000 | 20.000 | 0.00349 | 1 | 50.0
0.074 | 0.158 | 0.000 | 20.000 | 0.00349 | 1 | 50.0
0.068 | 0.161 | 0.000 | 20.000 | 0.00349 | 1 | 50.0
0.063 | 0.163 | 0.000 | 20.000 | 0.00349 | 1 | 50.0
0.057 | 0.165 | 0.000 | 20.000 | 0.00349 | 1 | 50.0
0.051 | 0.167 | 0.000 | 20.000 | 0.00349 | 1 | 50.0
0.045 | 0.169 | 0.000 | 20.000 | 0.00349 | 1 | 50.0
0.039 | 0.170 | 0.000 | 20.000 | 0.00349 | 1 | 50.0
0.033 | 0.171 | 0.000 | 20.000 | 0.00349 | 1 | 50.0
0.027 | 0.172 | 0.000 | 20.000 | 0.00349 | 1 | 50.0
0.021 | 0.173 | 0.000 | 20.000 | 0.00349 | 1 | 50.0
0.015 | 0.174 | 0.000 | 20.000 | 0.00349 | 1 | 50.0
0.009 | 0.174 | 0.000 | 20.000 | 0.00349 | 1 | 50.0
0.003 | 0.174 | 0.000 | 20.000 | 0.00349 | 1 | 50.0
-0.003 | 0.174 | 0.000 | 20.000 | 0.00349 | 1 | 50.0
-0.009 | 0.174 | 0.000 | 20.000 | 0.00349 | 1 | 50.0
-0.015 | 0.174 | 0.000 | 20.000 | 0.00349 | 1 | 50.0
-0.021 | 0.173 | 0.000 | 20.000 | 0.00349 | 1 | 50.0
-0.027 | 0.172 | 0.000 | 20.000 | 0.00349 | 1 | 50.0
-0.033 | 0.171 | 0.000 | 20.000 | 0.00349 | 1 | 50.0
-0.039 | 0.170 | 0.000 | 20.000 | 0.00349 | 1 | 50.0
-0.045 | 0.169 | 0.000 | 20.000 | 0.00349 | 1 | 50.0
-0.051 | 0.167 | 0.000 | 20.000 | 0.00349 | 1 | 50.0
-0.057 | 0.165 | 0.000 | 20.000 | 0.00349 | 1 | 50.0
-0.063 | 0.163 | 0.000 | 20.000 | 0.00349 | 1 | 50.0
-0.068 | 0.161 | 0.000 | 20.000 | 0.00349 | 1 | 50.0
-0.074 | 0.158 | 0.000 | 20.000 | 0.00349 | 1 | 50.0
-0.079 | 0.156 | 0.000 | 20.000 | 0.00349 | 1 | 50.0
-0.085 | 0.153 | 0.000 | 20.000 | 0.00349 | 1 | 50.0
-0.090 | 0.150 | 0.000 | 20.000 | 0.00349 | 1 | 50.0
-0.095 | 0.146 | 0.000 | 20.000 | 0.00349 | 1 | 50.0
-0.100 | 0.143 | 0.000 | 20.000 | 0.00349 | 1 | 50.0
-0.105 | 0.139 | 0.000 | 20.000 | 0.00349 | 1 | 50.0
-0.110 | 0.136 | 0.000 | 20.000 | 0.00349 | 1 | 50.0
-0.114 | 0.132 | 0.000 | 20.000 | 0.00349 | 1 | 50.0
-0.119 | 0.128 | 0.000 | 20.000 | 0.00349 | 1 | 50.0
-0.123 | 0.123 | 0.000 | 20.000 | 0.00349 | 1 | 50.0
-0.128 | 0.119 | 0.000 | 20.000 | 0.00349 | 1 | 50.0
-0.132 | 0.114 | 0.000 | 20.000 | 0.00349 | 1 | 50.0
-0.136 | 0.110 | 0.000 | 20.000 | 0.00349 | 1 | 50.0
-0.139 | 0.105 | 0.000 | 20.000 | 0.00349 | 1 | 50.0
-0.143 | 0.100 | 0.000 | 20.000 | 0.00349 | 1 | 50.0
-0.146 | 0.095 | 0.000 | 20.000 | 0.00349 | 1 | 50.0
-0.150 | 0.090 | 0.000 | 20.000 | 0.00349 | 1 | 50.0
-0.153 | 0.085 | 0.000 | 20.000 | 0.00349 | 1 | 50.0
-0.156 | 0.079 | 0.000 | 20.000 | 0.00349 | 1 | 50.0
-0.158 | 0.074 | 0.000 | 20.000 | 0.00349 | 1 | 50.0
-0.161 | 0.068 | 0.000 | 20.000 | 0.00349 | 1 | 50.0
-0.163 | 0.063 | 0.000 | 20.000 | 0.00349 | 1 | 50.0
-0.165 | 0.057 | 0.000 | 20.000 | 0.00349 | 1 | 50.0
-0.167 | 0.051 | 0.000 | 20.000 | 0.00349 | 1 | 50.0
-0.169 | 0.045 | 0.000 | 20.000 | 0.00349 | 1 | 50.0
-0.170 | 0.039 | 0.000 | 20.000 | 0.00349 | 1 | 50.0
-0.171 | 0.033 | 0.000 | 20.000 | 0.00349 | 1 | 50.0
-0.172 | 0.027 | 0.000 | 20.000 | 0.00349 | 1 | 50.0
-0.173 | 0.021 | 0.000 | 20.000 | 0.00349 | 1 | 50.0
-0.174 | 0.015 | 0.000 | 20.000 | 0.00349 | 1 | 50.0
-0.174 | 0.009 | 0.000 | 20.000 | 0.00349 | 1 | 50.0
-0.174 | 0.003 | 0.000 | 20.000 | 0.00349 | 1 | 50.0
-0.174 | -0.003 | 0.000 | 20.000 | 0.00349 | 1 | 50.0
-0.174 | -0.009 | 0.000 | 20.000 | 0.00349 | 1 | 50.0
-0.174 | -0.015 | 0.000 | 20.000 | 0.00349 | 1 | 50.0
-0.173 | -0.021 | 0.000 | 20.000 | 0.00349 | 1 | 50.0
-0.172 | -0.027 | 0.000 | 20.000 | 0.00349 | 1 | 50.0
-0.171 | -0.033 | 0.000 | 20.000 | 0.00349 | 1 | 50.0
-0.170 | -0.039 | 0.000 | 20.000 | 0.00349 | 1 | 50.0
-0.169 | -0.045 | 0.000 | 20.000 | 0.00349 | 1 | 50.0
-0.167 | -0.051 | 0.000 | 20.000 | 0.00349 | 1 | 50.0
-0.165 | -0.057 | 0.000 | 20.000 | 0.00349 | 1 | 50.0
-0.163 | -0.063 | 0.000 | 20.000 | 0.00349 | 1 | 50.0
-0.161 | -0.068 | 0.000 | 20.000 | 0.00349 | 1 | 50.0
-0.158 | -0.074 | 0.000 | 20.000 | 0.00349 | 1 | 50.0
-0.156 | -0.079 | 0.000 | 20.000 | 0.00349 | 1 | 50.0
-0.153 | -0.085 | 0.000 | 20.000 | 0.00349 | 1 | 50.0
-0.150 | -0.090 | 0.000 | 20.000 | 0.00349 | 1 | 50.0
-0.146 | -0.095 | 0.000 | 20.000 | 0.00349 | 1 | 50.0
-0.143 | -0.100 | 0.000 | 20.000 | 0.00349 | 1 | 50.0
-0.139 | -0.105 | 0.000 | 20.000 | 0.00349 | 1 | 50.0
-0.136 | -0.110 | 0.000 | 20.000 | 0.00349 | 1 | 50.0
-0.132 | -0.114 | 0.000 | 20.000 | 0.00349 | 1 | 50.0
-0.128 | -0.119 | 0.000 | 20.000 | 0.00349 | 1 | 50.0
-0.123 | -0.123 | 0.000 | 20.000 | 0.00349 | 1 | 50.0
-0.119 | -0.128 | 0.000 | 20.000 | 0.00349 | 1 | 50.0
-0.114 | -0.132 | 0.000 | 20.000 | 0.00349 | 1 | 50.0
-0.110 | -0.136 | 0.000 | 20.000 | 0.00349 | 1 | 50.0
-0.105 | -0.139 | 0.000 | 20.000 | 0.00349 | 1 | 50.0
-0.100 | -0.143 | 0.000 | 20.000 | 0.00349 | 1 | 50.0
-0.095 | -0.146 | 0.000 | 20.000 | 0.00349 | 1 | 50.0
-0.090 | -0.150 | 0.000 | 20.000 | 0.00349 | 1 | 50.0
-0.085 | -0.153 | 0.000 | 20.000 | 0.00349 | 1 | 50.0
-0.079 | -0.156 | 0.000 | 20.000 | 0.00349 | 1 | 50.0
-0.074 | -0.158 | 0.000 | 20.000 | 0.00349 | 1 | 50.0
-0.068 | -0.161 | 0.000 | 20.000 | 0.00349 | 1 | 50.0
-0.063 | -0.163 | 0.000 | 20.000 | 0.00349 | 1 | 50.0
-0.057 | -0.165 | 0.000 | 20.000 | 0.00349 | 1 | 50.0
-0.051 | -0.167 | 0.000 | 20.000 | 0.00349 | 1 | 50.0
-0.045 | -0.169 | 0.000 | 20.000 | 0.00349 | 1 | 50.0
-0.039 | -0.170 | 0.000 | 20.000 | 0.00349 | 1 | 50.0
-0.033 | -0.171 | 0.000 | 20.000 | 0.00349 | 1 | 50.0
-0.027 | -0.172 | 0.000 | 20.000 | 0.00349 | 1 | 50.0
-0.021 | -0.173 | 0.000 | 20.000 | 0.00349 | 1 | 50.0
-0.015 | -0.174 | 0.000 | 20.000 | 0.00349 | 1 | 50.0
-0.009 | -0.174 | 0.000 | 20.000 | 0.00349 | 1 | 50.0
-0.003 | -0.174 | 0.000 | 20.000 | 0.00349 | 1 | 50.0
0.003 | -0.174 | 0.000 | 20.000 | 0.00349 | 1 | 50.0
0.009 | -0.174 | 0.000 | 20.000 | 0.00349 | 1 | 50.0
0.015 | -0.174 | 0.000 | 20.000 | 0.00349 | 1 | 50.0
0.021 | -0.173 | 0.000 | 20.000 | 0.00349 | 1 | 50.0
0.027 | -0.172 | 0.000 | 20.000 | 0.00349 | 1 | 50.0
0.033 | -0.171 | 0.000 | 20.000 | 0.00349 | 1 | 50.0
0.039 | -0.170 | 0.000 | 20.000 | 0.00349 | 1 | 50.0
0.045 | -0.169 | 0.000 | 20.000 | 0.00349 | 1 | 50.0
0.051 | -0.167 | 0.000 | 20.000 | 0.00349 | 1 | 50.0
0.057 | -0.165 | 0.000 | 20.000 | 0.00349 | 1 | 50.0
0.063 | -0.163 | 0.000 | 20.000 | 0.00349 | 1 | 50.0
0.068 | -0.161 | 0.000 | 20.000 | 0.00349 | 1 | 50.0
0.074 | -0.158 | 0.000 | 20.000 | 0.00349 | 1 | 50.0
0.079 | -0.156 | 0.000 | 20.000 | 0.00349 | 1 | 50.0
0.085 | -0.153 | 0.000 | 20.000 | 0.00349 | 1 | 50.0
0.090 | -0.150 | 0.000 | 20.000 | 0.00349 | 1 | 50.0
0.095 | -0.146 | 0.000 | 20.000 | 0.00349 | 1 | 50.0
0.100 | -0.143 | 0.000 | 20.000 | 0.00349 | 1 | 50.0
0.105 | -0.139 | 0.000 | 20.000 | 0.00349 | 1 | 50.0
0.110 | -0.136 | 0.000 | 20.000 | 0.00349 | 1 | 50.0
0.114 | -0.132 | 0.000 | 20.000 | 0.00349 | 1 | 50.0
0.119 | -0.128 | 0.000 | 20.000 | 0.00349 | 1 | 50.0
0.123 | -0.123 | 0.000 | 20.000 | 0.00349 | 1 | 50.0
0.128 | -0.119 | 0.000 | 20.000 | 0.00349 | 1 | 50.0
0.132 | -0.114 | 0.000 | 20.000 | 0.00349 | 1 | 50.0
0.136 | -0.110 | 0.000 | 20.000 | 0.00349 | 1 | 50.0
0.139 | -0.105 | 0.000 | 20.000 | 0.00349 | 1 | 50.0
0.143 | -0.100 | 0.000 | 20.000 | 0.00349 | 1 | 50.0
0.146 | -0.095 | 0.000 | 20.000 | 0.00349 | 1 | 50.0
0.150 | -0.090 | 0.000 | 20.000 | 0.00349 | 1 | 50.0
0.153 | -0.085 | 0.000 | 20.000 | 0.00349 | 1 | 50.0
0.156 | -0.079 | 0.000 | 20.000 | 0.00349 | 1 | 50.0
0.158 | -0.074 | 0.000 | 20.000 | 0.00349 | 1 | 50.0
0.161 | -0.068 | 0.000 | 20.000 | 0.00349 | 1 | 50.0
0.163 | -0.063 | 0.000 | 20.000 | 0.00349 | 1 | 50.0
0.165 | -0.057 | 0.000 | 20.000 | 0.00349 | 1 | 50.0
0.167 | -0.051 | 0.000 | 20.000 | 0.00349 | 1 | 50.0
0.169 | -0.045 | 0.000 | 20.000 | 0.00349 | 1 | 50.0
0.170 | -0.039 | 0.000 | 20.000 | 0.00349 | 1 | 50.0
0.171 | -0.033 | 0.000 | 20.000 | 0.00349 | 1 | 50.0
0.172 | -0.027 | 0.000 | 20.000 | 0.00349 | 1 | 50.0
0.173 | -0.021 | 0.000 | 20.000 | 0.00349 | 1 | 50.0
0.174 | -0.015 | 0.000 | 20.000 | 0.00349 | 1 | 50.0
0.174 | -0.009 | 0.000 | 20.000 | 0.00349 | 1 | 50.0
0.174 | -0.003 | 0.000 | 20.000 | 0.00349 | 1 | 50.0
0.000 | 0.000 | 3.800 | 20.000 | 0.00000 | 1 | 50.0
0.000 | 5.000 | 0.000 | 20.000 | 0.00000 | 1 | 50.0
0.000 | -15.000 | 0.000 | 20.000 | 0.00000 | 1 | 50.0
0.000 | 0.000 | -3.800 | 20.000 | 0.00000 | 1 | 50.0
0.523 | 0.009 | 0.000 | 20.000 | 0.01047 | 1 | 50.0
0.523 | 0.027 | 0.000 | 20.000 | 0.01047 | 1 | 50.0
0.522 | 0.046 | 0.000 | 20.000 | 0.01047 | 1 | 50.0
0.520 | 0.064 | 0.000 | 20.000 | 0.01047 | 1 | 50.0
0.517 | 0.082 | 0.000 | 20.000 | 0.01047 | 1 | 50.0
0.514 | 0.100 | 0.000 | 20.000 | 0.01047 | 1 | 50.0
0.510 | 0.118 | 0.000 | 20.000 | 0.01047 | 1 | 50.0
0.506 | 0.136 | 0.000 | 20.000 | 0.01047 | 1 | 50.0
0.501 | 0.153 | 0.000 | 20.000 | 0.01047 | 1 | 50.0
0.495 | 0.170 | 0.000 | 20.000 | 0.01047 | 1 | 50.0
0.489 | 0.188 | 0.000 | 20.000 | 0.01047 | 1 | 50.0
0.482 | 0.205 | 0.000 | 20.000 | 0.01047 | 1 | 50.0
0.475 | 0.221 | 0.000 | 20.000 | 0.01047 | 1 | 50.0
0.467 | 0.238 | 0.000 | 20.000 | 0.01047 | 1 | 50.0
0.458 | 0.254 | 0.000 | 20.000 | 0.01047 | 1 | 50.0
0.449 | 0.270 | 0.000 | 20.000 | 0.01047 | 1 | 50.0
0.439 | 0.285 | 0.000 | 20.000 | 0.01047 | 1 | 50.0
0.429 | 0.300 | 0.000 | 20.000 | 0.01047 | 1 | 50.0
0.418 | 0.315 | 0.000 | 20.000 | 0.01047 | 1 | 50.0
0.407 | 0.329 | 0.000 | 20.000 | 0.01047 | 1 | 50.0
0.395 | 0.343 | 0.000 | 20.000 | 0.01047 | 1 | 50.0
0.383 | 0.357 | 0.000 | 20.000 | 0.01047 | 1 | 50.0
0.370 | 0.370 | 0.000 | 20.000 | 0.01047 | 1 | 50.0
0.357 | 0.383 | 0.000 | 20.000 | 0.01047 | 1 | 50.0
0.343 | 0.395 | 0.000 | 20.000 | 0.01047 | 1 | 50.0
0.329 | 0.407 | 0.000 | 20.000 | 0.01047 | 1 | 50.0
0.315 | 0.418 | 0.000 | 20.000 | 0.01047 | 1 | 50.0
0.300 | 0.429 | 0.000 | 20.000 | 0.01047 | 1 | 50.0
0.285 | 0.439 | 0.000 | 20.000 | 0.01047 | 1 | 50.0
0.270 | 0.449 | 0.000 | 20.000 | 0.01047 | 1 | 50.0
0.254 | 0.458 | 0.000 | 20.000 | 0.01047 | 1 | 50.0
0.238 | 0.467 | 0.000 | 20.000 | 0.01047 | 1 | 50.0
0.221 | 0.475 | 0.000 | 20.000 | 0.01047 | 1 | 50.0
0.205 | 0.482 | 0.000 | 20.000 | 0.01047 | 1 | 50.0
0.188 | 0.489 | 0.000 | 20.000 | 0.01047 | 1 | 50.0
0.170 | 0.495 | 0.000 | 20.000 | 0.01047 | 1 | 50.0
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

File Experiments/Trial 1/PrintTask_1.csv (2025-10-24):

X | Y | Z | Speed | E | Mode | NozzleTemp
210 | 270 | -90 | 40 | 0 | 0 | 30
210 | 270 | -90 | 2 | 10 | 0 | 30
95 | 120.5 | -99 | 20 | 10 | 0 | 30
95 | 220.5 | -99 | 20 | 11 | 0 | 30
105 | 220.5 | -95 | 20 | 11 | 0 | 30
115 | 120.5 | -98.8 | 20 | 11 | 0 | 30
115 | 220.5 | -98.8 | 20 | 12 | 0 | 30
125 | 220.5 | -95 | 20 | 12 | 0 | 30
135 | 120.5 | -98.6 | 20 | 12 | 0 | 30
135 | 220.5 | -98.6 | 20 | 13 | 0 | 30
145 | 220.5 | -95 | 20 | 13 | 0 | 30
155 | 120.5 | -98.4 | 20 | 13 | 0 | 30
155 | 220.5 | -98.4 | 20 | 14 | 0 | 30
165 | 220.5 | -95 | 20 | 14 | 0 | 30
175 | 120.5 | -98.2 | 20 | 14 | 0 | 30
175 | 220.5 | -98.2 | 20 | 15 | 0 | 30
185 | 220.5 | -95 | 20 | 15 | 0 | 30
210 | 0 | 0 | 30 | 15 | 0 | 30

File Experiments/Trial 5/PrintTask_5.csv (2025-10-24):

X | Y | Z | Speed | E | Mode | NozzleTemp
210 | 270 | -90 | 40 | 0 | 0 | 30
210 | 270 | -90 | 2 | 10 | 0 | 30
135 | 170.5 | -99.2 | 30 | 10 | 0 | 30
135 | 170.5 | -90 | 20 | 10 | 0 | 30
100 | 115 | -90 | 20 | 10 | 0 | 30
100 | 115 | -98.8 | 20 | 10 | 0 | 30
100 | 115 | -98.8 | 20 | 10 | 0 | 30
100 | 145 | -98.8 | 20 | 10.6 | 0 | 30
104 | 145 | -98.8 | 20 | 10.6 | 0 | 30
104 | 115 | -98.8 | 20 | 11.2 | 0 | 30
108 | 115 | -98.8 | 20 | 11.2 | 0 | 30
108 | 145 | -98.8 | 20 | 11.8 | 0 | 30
112 | 145 | -98.8 | 20 | 11.8 | 0 | 30
112 | 115 | -98.8 | 20 | 12.4 | 0 | 30
116 | 115 | -98.8 | 20 | 12.4 | 0 | 30
116 | 145 | -98.8 | 20 | 13 | 0 | 30
120 | 145 | -98.8 | 20 | 13 | 0 | 30
120 | 115 | -98.8 | 20 | 13.6 | 0 | 30
124 | 115 | -98.8 | 20 | 13.6 | 0 | 30
124 | 145 | -98.8 | 20 | 14.2 | 0 | 30
128 | 145 | -98.8 | 20 | 14.2 | 0 | 30
128 | 115 | -98.8 | 20 | 14.8 | 0 | 30
128 | 115 | -90 | 20 | 14.8 | 0 | 30
128 | 115 | -90 | 20 | 14.8 | 0 | 30
100 | 155 | -90 | 20 | 14.8 | 0 | 30
100 | 155 | -98.8 | 20 | 14.8 | 0 | 30
100 | 155 | -98.8 | 20 | 14.8 | 0 | 30
100 | 185 | -98.8 | 20 | 15.4 | 0 | 30
104 | 185 | -98.8 | 20 | 15.4 | 0 | 30
104 | 155 | -98.8 | 20 | 16 | 0 | 30
108 | 155 | -98.8 | 20 | 16 | 0 | 30
108 | 185 | -98.8 | 20 | 16.6 | 0 | 30
112 | 185 | -98.8 | 20 | 16.6 | 0 | 30
112 | 155 | -98.8 | 20 | 17.2 | 0 | 30
116 | 155 | -98.8 | 20 | 17.2 | 0 | 30
116 | 185 | -98.8 | 20 | 17.8 | 0 | 30
120 | 185 | -98.8 | 20 | 17.8 | 0 | 30
120 | 155 | -98.8 | 20 | 18.4 | 0 | 30
124 | 155 | -98.8 | 20 | 18.4 | 0 | 30
124 | 185 | -98.8 | 20 | 19 | 0 | 30
128 | 185 | -98.8 | 20 | 19 | 0 | 30
128 | 155 | -98.8 | 20 | 19.6 | 0 | 30
128 | 155 | -90 | 20 | 19.6 | 0 | 30
128 | 155 | -90 | 20 | 19.6 | 0 | 30
100 | 195 | -90 | 20 | 19.6 | 0 | 30
100 | 195 | -98.8 | 20 | 19.6 | 0 | 30
100 | 195 | -98.8 | 20 | 19.6 | 0 | 30
100 | 225 | -98.8 | 20 | 20.2 | 0 | 30
104 | 225 | -98.8 | 20 | 20.2 | 0 | 30
104 | 195 | -98.8 | 20 | 20.8 | 0 | 30
108 | 195 | -98.8 | 20 | 20.8 | 0 | 30
108 | 225 | -98.8 | 20 | 21.4 | 0 | 30
112 | 225 | -98.8 | 20 | 21.4 | 0 | 30
112 | 195 | -98.8 | 20 | 22 | 0 | 30
116 | 195 | -98.8 | 20 | 22 | 0 | 30
116 | 225 | -98.8 | 20 | 22.6 | 0 | 30
120 | 225 | -98.8 | 20 | 22.6 | 0 | 30
120 | 195 | -98.8 | 20 | 23.2 | 0 | 30
124 | 195 | -98.8 | 20 | 23.2 | 0 | 30
124 | 225 | -98.8 | 20 | 23.8 | 0 | 30
128 | 225 | -98.8 | 20 | 23.8 | 0 | 30
128 | 195 | -98.8 | 20 | 24.4 | 0 | 30
128 | 195 | -90 | 20 | 24.4 | 0 | 30
128 | 195 | -90 | 20 | 24.4 | 0 | 30
100 | 115 | -90 | 20 | 24.4 | 0 | 30
100 | 115 | -97.8 | 20 | 24.4 | 0 | 30
100 | 115 | -97.8 | 20 | 24.4 | 0 | 30
130 | 115 | -97.8 | 20 | 25 | 0 | 30
130 | 119 | -97.8 | 20 | 25 | 0 | 30
100 | 119 | -97.8 | 20 | 25.6 | 0 | 30
100 | 123 | -97.8 | 20 | 25.6 | 0 | 30
130 | 123 | -97.8 | 20 | 26.2 | 0 | 30
130 | 127 | -97.8 | 20 | 26.2 | 0 | 30
100 | 127 | -97.8 | 20 | 26.8 | 0 | 30
100 | 131 | -97.8 | 20 | 26.8 | 0 | 30
130 | 131 | -97.8 | 20 | 27.4 | 0 | 30
130 | 135 | -97.8 | 20 | 27.4 | 0 | 30
100 | 135 | -97.8 | 20 | 28 | 0 | 30
100 | 139 | -97.8 | 20 | 28 | 0 | 30
130 | 139 | -97.8 | 20 | 28.6 | 0 | 30
130 | 143 | -97.8 | 20 | 28.6 | 0 | 30
100 | 143 | -97.8 | 20 | 29.2 | 0 | 30
100 | 143 | -90 | 20 | 29.2 | 0 | 30
100 | 143 | -90 | 20 | 29.2 | 0 | 30
100 | 155 | -90 | 20 | 29.2 | 0 | 30
100 | 155 | -97.3 | 20 | 29.2 | 0 | 30
100 | 155 | -97.3 | 20 | 29.2 | 0 | 30
130 | 155 | -97.3 | 20 | 29.8 | 0 | 30
130 | 159 | -97.3 | 20 | 29.8 | 0 | 30
100 | 159 | -97.3 | 20 | 30.4 | 0 | 30
100 | 163 | -97.3 | 20 | 30.4 | 0 | 30
130 | 163 | -97.3 | 20 | 31 | 0 | 30
130 | 167 | -97.3 | 20 | 31 | 0 | 30
100 | 167 | -97.3 | 20 | 31.6 | 0 | 30
100 | 171 | -97.3 | 20 | 31.6 | 0 | 30
130 | 171 | -97.3 | 20 | 32.2 | 0 | 30
130 | 175 | -97.3 | 20 | 32.2 | 0 | 30
100 | 175 | -97.3 | 20 | 32.8 | 0 | 30
100 | 179 | -97.3 | 20 | 32.8 | 0 | 30
130 | 179 | -97.3 | 20 | 33.4 | 0 | 30
130 | 183 | -97.3 | 20 | 33.4 | 0 | 30
100 | 183 | -97.3 | 20 | 34 | 0 | 30
100 | 183 | -90 | 20 | 34 | 0 | 30
100 | 183 | -90 | 20 | 34 | 0 | 30
100 | 195 | -90 | 20 | 34 | 0 | 30
100 | 195 | -96.8 | 20 | 34 | 0 | 30
100 | 195 | -96.8 | 20 | 34 | 0 | 30
130 | 195 | -96.8 | 20 | 34.6 | 0 | 30
130 | 199 | -96.8 | 20 | 34.6 | 0 | 30
100 | 199 | -96.8 | 20 | 35.2 | 0 | 30
100 | 203 | -96.8 | 20 | 35.2 | 0 | 30
130 | 203 | -96.8 | 20 | 35.8 | 0 | 30
130 | 207 | -96.8 | 20 | 35.8 | 0 | 30
100 | 207 | -96.8 | 20 | 36.4 | 0 | 30
100 | 211 | -96.8 | 20 | 36.4 | 0 | 30
130 | 211 | -96.8 | 20 | 37 | 0 | 30
130 | 215 | -96.8 | 20 | 37 | 0 | 30
100 | 215 | -96.8 | 20 | 37.6 | 0 | 30
100 | 219 | -96.8 | 20 | 37.6 | 0 | 30
130 | 219 | -96.8 | 20 | 38.2 | 0 | 30
130 | 223 | -96.8 | 20 | 38.2 | 0 | 30
100 | 223 | -96.8 | 20 | 38.8 | 0 | 30
100 | 223 | -90 | 20 | 38.8 | 0 | 30
100 | 223 | -90 | 20 | 38.8 | 0 | 30
100 | 115 | -90 | 20 | 38.8 | 0 | 30
100 | 115 | -96.8 | 20 | 38.8 | 0 | 30
100 | 115 | -96.8 | 20 | 38.8 | 0 | 30
100 | 145 | -96.8 | 20 | 39.4 | 0 | 30
104 | 145 | -96.8 | 20 | 39.4 | 0 | 30
104 | 115 | -96.8 | 20 | 40 | 0 | 30
108 | 115 | -96.8 | 20 | 40 | 0 | 30
108 | 145 | -96.8 | 20 | 40.6000000000001 | 0 | 30
112 | 145 | -96.8 | 20 | 40.6000000000001 | 0 | 30
112 | 115 | -96.8 | 20 | 41.2000000000001 | 0 | 30
116 | 115 | -96.8 | 20 | 41.2000000000001 | 0 | 30
116 | 145 | -96.8 | 20 | 41.8000000000001 | 0 | 30
120 | 145 | -96.8 | 20 | 41.8000000000001 | 0 | 30
120 | 115 | -96.8 | 20 | 42.4000000000001 | 0 | 30
124 | 115 | -96.8 | 20 | 42.4000000000001 | 0 | 30
124 | 145 | -96.8 | 20 | 43.0000000000001 | 0 | 30
128 | 145 | -96.8 | 20 | 43.0000000000001 | 0 | 30
128 | 115 | -96.8 | 20 | 43.6000000000001 | 0 | 30
128 | 115 | -90 | 20 | 43.6000000000001 | 0 | 30
128 | 115 | -90 | 20 | 43.6000000000001 | 0 | 30
100 | 155 | -90 | 20 | 43.6000000000001 | 0 | 30
100 | 155 | -95.8 | 20 | 43.6000000000001 | 0 | 30
100 | 155 | -95.8 | 20 | 43.6000000000001 | 0 | 30
100 | 185 | -95.8 | 20 | 44.2000000000001 | 0 | 30
104 | 185 | -95.8 | 20 | 44.2000000000001 | 0 | 30
104 | 155 | -95.8 | 20 | 44.8000000000001 | 0 | 30
108 | 155 | -95.8 | 20 | 44.8000000000001 | 0 | 30
108 | 185 | -95.8 | 20 | 45.4000000000001 | 0 | 30
112 | 185 | -95.8 | 20 | 45.4000000000001 | 0 | 30
112 | 155 | -95.8 | 20 | 46.0000000000001 | 0 | 30
116 | 155 | -95.8 | 20 | 46.0000000000001 | 0 | 30
116 | 185 | -95.8 | 20 | 46.6000000000001 | 0 | 30
120 | 185 | -95.8 | 20 | 46.6000000000001 | 0 | 30
120 | 155 | -95.8 | 20 | 47.2000000000001 | 0 | 30
124 | 155 | -95.8 | 20 | 47.2000000000001 | 0 | 30
124 | 185 | -95.8 | 20 | 47.8000000000001 | 0 | 30
128 | 185 | -95.8 | 20 | 47.8000000000001 | 0 | 30
128 | 155 | -95.8 | 20 | 48.4000000000001 | 0 | 30
128 | 155 | -90 | 20 | 48.4000000000001 | 0 | 30
128 | 155 | -90 | 20 | 48.4000000000001 | 0 | 30
100 | 195 | -90 | 20 | 48.4000000000001 | 0 | 30
100 | 195 | -94.8 | 20 | 48.4000000000001 | 0 | 30
100 | 195 | -94.8 | 20 | 48.4000000000001 | 0 | 30
100 | 225 | -94.8 | 20 | 49.0000000000001 | 0 | 30
104 | 225 | -94.8 | 20 | 49.0000000000001 | 0 | 30
104 | 195 | -94.8 | 20 | 49.6000000000001 | 0 | 30
108 | 195 | -94.8 | 20 | 49.6000000000001 | 0 | 30
108 | 225 | -94.8 | 20 | 50.2000000000001 | 0 | 30
112 | 225 | -94.8 | 20 | 50.2000000000001 | 0 | 30
112 | 195 | -94.8 | 20 | 50.8000000000001 | 0 | 30
116 | 195 | -94.8 | 20 | 50.8000000000001 | 0 | 30
116 | 225 | -94.8 | 20 | 51.4000000000001 | 0 | 30
120 | 225 | -94.8 | 20 | 51.4000000000001 | 0 | 30
120 | 195 | -94.8 | 20 | 52.0000000000001 | 0 | 30
124 | 195 | -94.8 | 20 | 52.0000000000001 | 0 | 30
124 | 225 | -94.8 | 20 | 52.6000000000001 | 0 | 30
128 | 225 | -94.8 | 20 | 52.6000000000001 | 0 | 30
128 | 195 | -94.8 | 20 | 53.2000000000001 | 0 | 30
128 | 195 | -90 | 20 | 53.2000000000001 | 0 | 30
128 | 195 | -90 | 20 | 53.2000000000001 | 0 | 30
100 | 115 | -90 | 20 | 53.2000000000001 | 0 | 30
100 | 115 | -95.8 | 20 | 53.2000000000001 | 0 | 30
100 | 115 | -95.8 | 20 | 53.2000000000001 | 0 | 30
130 | 115 | -95.8 | 20 | 53.8000000000001 | 0 | 30
130 | 119 | -95.8 | 20 | 53.8000000000001 | 0 | 30
100 | 119 | -95.8 | 20 | 54.4000000000001 | 0 | 30
100 | 123 | -95.8 | 20 | 54.4000000000001 | 0 | 30
130 | 123 | -95.8 | 20 | 55.0000000000001 | 0 | 30
130 | 127 | -95.8 | 20 | 55.0000000000001 | 0 | 30
100 | 127 | -95.8 | 20 | 55.6000000000001 | 0 | 30
100 | 131 | -95.8 | 20 | 55.6000000000001 | 0 | 30
130 | 131 | -95.8 | 20 | 56.2000000000001 | 0 | 30
130 | 135 | -95.8 | 20 | 56.2000000000001 | 0 | 30
100 | 135 | -95.8 | 20 | 56.8000000000001 | 0 | 30
100 | 139 | -95.8 | 20 | 56.8000000000001 | 0 | 30
130 | 139 | -95.8 | 20 | 57.4000000000001 | 0 | 30
130 | 143 | -95.8 | 20 | 57.4000000000001 | 0 | 30
100 | 143 | -95.8 | 20 | 58.0000000000001 | 0 | 30
100 | 143 | -90 | 20 | 58.0000000000001 | 0 | 30
100 | 143 | -90 | 20 | 58.0000000000001 | 0 | 30
100 | 155 | -90 | 20 | 58.0000000000001 | 0 | 30
100 | 155 | -94.3 | 20 | 58.0000000000001 | 0 | 30
100 | 155 | -94.3 | 20 | 58.0000000000001 | 0 | 30
130 | 155 | -94.3 | 20 | 58.6000000000001 | 0 | 30
130 | 159 | -94.3 | 20 | 58.6000000000001 | 0 | 30
100 | 159 | -94.3 | 20 | 59.2000000000001 | 0 | 30
100 | 163 | -94.3 | 20 | 59.2000000000001 | 0 | 30
130 | 163 | -94.3 | 20 | 59.8000000000001 | 0 | 30
130 | 167 | -94.3 | 20 | 59.8000000000001 | 0 | 30
100 | 167 | -94.3 | 20 | 60.4000000000001 | 0 | 30
100 | 171 | -94.3 | 20 | 60.4000000000001 | 0 | 30
130 | 171 | -94.3 | 20 | 61.0000000000001 | 0 | 30
130 | 175 | -94.3 | 20 | 61.0000000000001 | 0 | 30
100 | 175 | -94.3 | 20 | 61.6000000000001 | 0 | 30
100 | 179 | -94.3 | 20 | 61.6000000000001 | 0 | 30
130 | 179 | -94.3 | 20 | 62.2000000000001 | 0 | 30
130 | 183 | -94.3 | 20 | 62.2000000000001 | 0 | 30
100 | 183 | -94.3 | 20 | 62.8000000000001 | 0 | 30
100 | 183 | -90 | 20 | 62.8000000000001 | 0 | 30
100 | 183 | -90 | 20 | 62.8000000000001 | 0 | 30
100 | 195 | -90 | 20 | 62.8000000000001 | 0 | 30
100 | 195 | -92.8 | 20 | 62.8000000000001 | 0 | 30
100 | 195 | -92.8 | 20 | 62.8000000000001 | 0 | 30
130 | 195 | -92.8 | 20 | 63.4000000000001 | 0 | 30
130 | 199 | -92.8 | 20 | 63.4000000000001 | 0 | 30
100 | 199 | -92.8 | 20 | 64.0000000000001 | 0 | 30
100 | 203 | -92.8 | 20 | 64.0000000000001 | 0 | 30
130 | 203 | -92.8 | 20 | 64.6000000000001 | 0 | 30
130 | 207 | -92.8 | 20 | 64.6000000000001 | 0 | 30
100 | 207 | -92.8 | 20 | 65.2000000000001 | 0 | 30
100 | 211 | -92.8 | 20 | 65.2000000000001 | 0 | 30
130 | 211 | -92.8 | 20 | 65.8000000000001 | 0 | 30
130 | 215 | -92.8 | 20 | 65.8000000000001 | 0 | 30
100 | 215 | -92.8 | 20 | 66.4000000000001 | 0 | 30
100 | 219 | -92.8 | 20 | 66.4000000000001 | 0 | 30
130 | 219 | -92.8 | 20 | 67.0000000000001 | 0 | 30
130 | 223 | -92.8 | 20 | 67.0000000000001 | 0 | 30
100 | 223 | -92.8 | 20 | 67.6000000000001 | 0 | 30
100 | 223 | -90 | 20 | 67.6000000000001 | 0 | 30
210 | 0 | -90 | 20 | 67.6000000000001 | 0 | 30
210 | 0 | 0 | 40 | 67.6000000000001 | 0 | 30

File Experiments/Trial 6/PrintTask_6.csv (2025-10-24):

X | Y | Z | Speed | E | Mode | NozzleTemp
210 | 270 | -90 | 40 | 0 | 0 | 30
210 | 270 | -90 | 2 | 10 | 0 | 30
95 | 120.5 | -98.8 | 20 | 10 | 0 | 30
95 | 220.5 | -98.8 | 20 | 12 | 0 | 30
105 | 220.5 | -95 | 20 | 12 | 0 | 30
115 | 120.5 | -98.8 | 20 | 12 | 0 | 30
115 | 220.5 | -98.8 | 20 | 14 | 0 | 30
125 | 220.5 | -95 | 20 | 14 | 0 | 30
135 | 120.5 | -98.8 | 20 | 14 | 0 | 30
135 | 220.5 | -98.8 | 20 | 16 | 0 | 30
145 | 220.5 | -95 | 20 | 16 | 0 | 30
155 | 120.5 | -98.8 | 20 | 16 | 0 | 30
155 | 220.5 | -98.8 | 20 | 18 | 0 | 30
165 | 220.5 | -95 | 20 | 18 | 0 | 30
175 | 120.5 | -98.8 | 20 | 18 | 0 | 30
175 | 220.5 | -98.8 | 20 | 20 | 0 | 30
185 | 220.5 | -95 | 20 | 20 | 0 | 30
210 | 0 | 0 | 30 | 20 | 0 | 30

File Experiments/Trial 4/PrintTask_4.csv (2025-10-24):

X | Y | Z | Speed | E | Mode | NozzleTemp
210 | 270 | -90 | 40 | 0 | 0 | 30
210 | 270 | -90 | 2 | 10 | 0 | 30
100 | 115 | -98.8 | 20 | 10 | 0 | 30
100 | 165 | -98.8 | 20 | 11 | 0 | 30
103 | 165 | -95 | 20 | 11 | 0 | 30
103 | 115 | -98.8 | 20 | 11 | 0 | 30
103 | 165 | -98.8 | 20 | 12 | 0 | 30
106 | 165 | -95 | 20 | 12 | 0 | 30
106 | 115 | -98.8 | 20 | 12 | 0 | 30
106 | 165 | -98.8 | 20 | 13 | 0 | 30
109 | 165 | -95 | 20 | 13 | 0 | 30
109 | 115 | -98.8 | 20 | 13 | 0 | 30
109 | 165 | -98.8 | 20 | 14 | 0 | 30
112 | 165 | -95 | 20 | 14 | 0 | 30
100 | 175 | -98.8 | 20 | 14 | 0 | 30
100 | 225 | -98.8 | 20 | 15 | 0 | 30
103 | 225 | -95 | 20 | 15 | 0 | 30
103.5 | 175 | -98.8 | 20 | 15 | 0 | 30
103.5 | 225 | -98.8 | 20 | 16 | 0 | 30
106.5 | 225 | -95 | 20 | 16 | 0 | 30
107 | 175 | -98.8 | 20 | 16 | 0 | 30
107 | 225 | -98.8 | 20 | 17 | 0 | 30
110 | 225 | -95 | 20 | 17 | 0 | 30
110.5 | 175 | -98.8 | 20 | 17 | 0 | 30
110.5 | 225 | -98.8 | 20 | 18 | 0 | 30
113.5 | 225 | -95 | 20 | 18 | 0 | 30
130 | 115 | -98.8 | 20 | 18 | 0 | 30
130 | 165 | -98.8 | 20 | 19 | 0 | 30
133 | 165 | -95 | 20 | 19 | 0 | 30
134 | 115 | -98.8 | 20 | 19 | 0 | 30
134 | 165 | -98.8 | 20 | 20 | 0 | 30
137 | 165 | -95 | 20 | 20 | 0 | 30
138 | 115 | -98.8 | 20 | 20 | 0 | 30
138 | 165 | -98.8 | 20 | 21 | 0 | 30
141 | 165 | -95 | 20 | 21 | 0 | 30
142 | 115 | -98.8 | 20 | 21 | 0 | 30
142 | 165 | -98.8 | 20 | 22 | 0 | 30
145 | 165 | -95 | 20 | 22 | 0 | 30
130 | 175 | -98.8 | 20 | 22 | 0 | 30
130 | 225 | -98.8 | 20 | 23 | 0 | 30
133 | 225 | -95 | 20 | 23 | 0 | 30
134.5 | 175 | -98.8 | 20 | 23 | 0 | 30
134.5 | 225 | -98.8 | 20 | 24 | 0 | 30
137.5 | 225 | -95 | 20 | 24 | 0 | 30
139 | 175 | -98.8 | 20 | 24 | 0 | 30
139 | 225 | -98.8 | 20 | 25 | 0 | 30
142 | 225 | -95 | 20 | 25 | 0 | 30
143.5 | 175 | -98.8 | 20 | 25 | 0 | 30
143.5 | 225 | -98.8 | 20 | 26 | 0 | 30
146.5 | 225 | -95 | 20 | 26 | 0 | 30
160 | 115 | -98.8 | 20 | 26 | 0 | 30
160 | 165 | -98.8 | 20 | 27 | 0 | 30
163 | 165 | -95 | 20 | 27 | 0 | 30
165 | 115 | -98.8 | 20 | 27 | 0 | 30
165 | 165 | -98.8 | 20 | 28 | 0 | 30
168 | 165 | -95 | 20 | 28 | 0 | 30
170 | 115 | -98.8 | 20 | 28 | 0 | 30
170 | 165 | -98.8 | 20 | 29 | 0 | 30
173 | 165 | -95 | 20 | 29 | 0 | 30
175 | 115 | -98.8 | 20 | 29 | 0 | 30
175 | 165 | -98.8 | 20 | 30 | 0 | 30
178 | 165 | -95 | 20 | 30 | 0 | 30
160 | 175 | -98.8 | 20 | 30 | 0 | 30
160 | 225 | -98.8 | 20 | 31 | 0 | 30
163 | 225 | -95 | 20 | 31 | 0 | 30
165.5 | 175 | -98.8 | 20 | 31 | 0 | 30
165.5 | 225 | -98.8 | 20 | 32 | 0 | 30
168.5 | 225 | -95 | 20 | 32 | 0 | 30
171 | 175 | -98.8 | 20 | 32 | 0 | 30
171 | 225 | -98.8 | 20 | 33 | 0 | 30
174 | 225 | -95 | 20 | 33 | 0 | 30
176.5 | 175 | -98.8 | 20 | 33 | 0 | 30
176.5 | 225 | -98.8 | 20 | 34 | 0 | 30
179.5 | 225 | -95 | 20 | 34 | 0 | 30
210 | 0 | 0 | 40 | 34 | 0 | 30

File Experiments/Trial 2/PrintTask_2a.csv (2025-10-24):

X | Y | Z | Speed | E | Mode | NozzleTemp
210 | 270 | -90 | 40 | 0 | 0 | 30
210 | 270 | -90 | 2 | 10 | 0 | 30
90 | 120.5 | -98.8 | 20 | 10 | 0 | 30
90 | 220.5 | -98.8 | 20 | 11 | 0 | 30
96 | 220.5 | -95 | 20 | 11 | 0 | 30
102 | 120.5 | -98.8 | 20 | 11 | 0 | 30
102 | 220.5 | -98.8 | 20 | 12.5 | 0 | 30
108 | 220.5 | -95 | 20 | 12.5 | 0 | 30
114 | 120.5 | -98.8 | 20 | 12.5 | 0 | 30
114 | 220.5 | -98.8 | 20 | 14.5 | 0 | 30
120 | 220.5 | -95 | 20 | 14.5 | 0 | 30
126 | 120.5 | -98.8 | 20 | 14.5 | 0 | 30
126 | 220.5 | -98.8 | 20 | 17 | 0 | 30
132 | 220.5 | -95 | 20 | 17 | 0 | 30
138 | 120.5 | -98.8 | 20 | 17 | 0 | 30
138 | 220.5 | -98.8 | 25 | 17.8 | 0 | 30
144 | 220.5 | -95 | 20 | 17.8 | 0 | 30
150 | 120.5 | -98.8 | 20 | 17.8 | 0 | 30
150 | 220.5 | -98.8 | 25 | 19 | 0 | 30
156 | 220.5 | -95 | 20 | 19 | 0 | 30
162 | 120.5 | -98.8 | 20 | 19 | 0 | 30
162 | 220.5 | -98.8 | 25 | 20.6 | 0 | 30
168 | 220.5 | -95 | 20 | 20.6 | 0 | 30
174 | 120.5 | -98.8 | 20 | 20.6 | 0 | 30
174 | 220.5 | -98.8 | 25 | 22.6 | 0 | 30
180 | 220.5 | -95 | 20 | 22.6 | 0 | 30
210 | 0 | 0 | 40 | 22.6 | 0 | 30

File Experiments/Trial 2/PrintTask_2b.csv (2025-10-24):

X | Y | Z | Speed | E | Mode | NozzleTemp
210 | 270 | -90 | 40 | 0 | 0 | 30
210 | 270 | -90 | 2 | 10 | 0 | 30
90 | 120.5 | -98.8 | 20 | 10 | 0 | 30
90 | 220.5 | -98.8 | 30 | 10.667 | 0 | 30
96 | 220.5 | -95 | 20 | 10.667 | 0 | 30
102 | 120.5 | -98.8 | 20 | 10.667 | 0 | 30
102 | 220.5 | -98.8 | 30 | 11.667 | 0 | 30
108 | 220.5 | -95 | 20 | 11.667 | 0 | 30
114 | 120.5 | -98.8 | 20 | 11.667 | 0 | 30
114 | 220.5 | -98.8 | 30 | 13 | 0 | 30
120 | 220.5 | -95 | 20 | 13 | 0 | 30
126 | 120.5 | -98.8 | 20 | 13 | 0 | 30
126 | 220.5 | -98.8 | 30 | 14.667 | 0 | 30
132 | 220.5 | -95 | 20 | 14.667 | 0 | 30
138 | 120.5 | -98.8 | 20 | 14.667 | 0 | 30
138 | 220.5 | -98.8 | 35 | 15.238 | 0 | 30
144 | 220.5 | -95 | 20 | 15.238 | 0 | 30
150 | 120.5 | -98.8 | 20 | 15.238 | 0 | 30
150 | 220.5 | -98.8 | 35 | 16.095 | 0 | 30
156 | 220.5 | -95 | 20 | 16.095 | 0 | 30
162 | 120.5 | -98.8 | 20 | 16.095 | 0 | 30
162 | 220.5 | -98.8 | 35 | 17.238 | 0 | 30
168 | 220.5 | -95 | 20 | 17.238 | 0 | 30
174 | 120.5 | -98.8 | 20 | 17.238 | 0 | 30
174 | 220.5 | -98.8 | 35 | 18.667 | 0 | 30
180 | 220.5 | -95 | 20 | 18.667 | 0 | 30
210 | 0 | 0 | 40 | 18.667 | 0 | 30

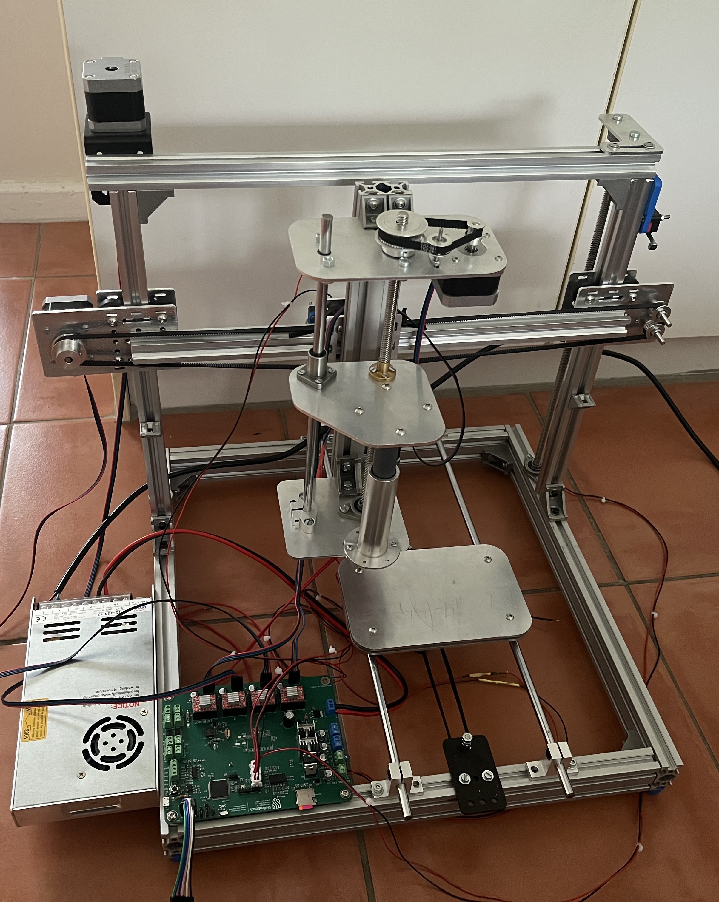
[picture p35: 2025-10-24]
Docs/Report/Development_of_a_Hydrogel_Extruder/figs/Printer2.jpg

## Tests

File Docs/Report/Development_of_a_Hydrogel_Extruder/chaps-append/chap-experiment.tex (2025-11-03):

\chapter{Experimental Calibration}
\section{Calibration Test Matrices}
{\small
\begin{longtable}{ccc}
\caption{Proposed Test Matrix for Optimal Nozzle height} \label{tab:heightmatrix} \\
\hline
\textbf{Test No.} & \textbf{Nozzle Height (mm)} \\
\hline
\endhead
\hline
1 & 0.2 \\
2 & 0.4 \\
3 & 0.6 \\
4 & 0.8 \\
5 & 1.0 \\
\hline
\end{longtable}
}

{\small
\begin{longtable}{ccc}
\caption{Proposed Test Matrix for Straight Line Experiment} \label{tab:linetestmatrix} \\
\hline
\textbf{Test No.} & \textbf{Printing Speed (mm/s)} & \textbf{Extrusion Speed (mm/s)} \\
\hline
1  & 20 & 0.2 \\
2  & 20 & 0.3 \\
3  & 20 & 0.4 \\
4  & 20 & 0.5 \\
5  & 25 & 0.2 \\
6  & 25 & 0.3 \\
7  & 25 & 0.4 \\
8  & 25 & 0.5 \\
9  & 30 & 0.2 \\
10 & 30 & 0.3 \\
11 & 30 & 0.4 \\
12 & 30 & 0.5 \\
13 & 35 & 0.2 \\
14 & 35 & 0.3 \\
15 & 35 & 0.4 \\
16 & 35 & 0.5 \\
\hline
\end{longtable}
}

{\small
\begin{longtable}{ccc}
\caption{Proposed Test Matrix for Curved Line Experiment} \label{tab:curvetestmatrix} \\
\hline
\textbf{Test No.} & \textbf{Line Radius (mm)} \\
\hline
\endhead
\hline
1  & 5 \\
2  & 15 \\
3  & 25 \\
4  & 35 \\
5  & 45 \\
\hline
\end{longtable}
}
{\small
\begin{longtable}{ccc}
\caption{Proposed Test Matrix for Optimal Spacing of Adjacent Lines} \label{tab:spacingmatrix} \\
\hline
\textbf{Test No.} & \textbf{Line Spacing (mm)} \\
\hline
\endhead
\hline
1 & 3.0 \\
2 & 3.5 \\
3 & 4.0 \\
4 & 4.5 \\
5 & 5.0 \\
6 & 5.5 \\
\hline
\end{longtable}
}
{\small
\begin{longtable}{ccc}
\caption{Proposed Test Matrix for Optimal Layer Stacking Offset} \label{tab:stackingmatrix} \\
\hline
\textbf{Test No.} & \textbf{Layer Offset (mm)} \\
\hline
\endhead
\hline
1 & 1.0 \\
2 & 1.5 \\
3 & 2.0 \\
\hline
\end{longtable}
}
\section{Measured Results}

{\small
\begin{longtable}{>{\raggedright\arraybackslash}p{1cm} 
                  >{\centering\arraybackslash}p{2cm} 
                  >{\centering\arraybackslash}p{2cm} 
                  >{\centering\arraybackslash}p{2cm} 
                  >{\centering\arraybackslash}p{1.5cm} 
                  >{\centering\arraybackslash}p{1.5cm}
                  >{\centering\arraybackslash}p{1.5cm}}
\caption{Calibration Phase 1 - Nozzle Height Test Results}  \label{tab:heightResults} \\
\hline
\textbf{Test No.} & \textbf{Nozzle Height (mm)} & \textbf{Length (mm)} & \textbf{Mean Width (mm)}  & \textbf{Std Dev Width (mm)} \\
\hline
\endhead
\hline
1  & 0.2 & 88 & 2.9 & 0.71 \\
2  & 0.4 & 94 & 3.0 & 0.33 \\
3  & 0.6 & 93 & 3.0 & 0.53 \\
4  & 0.8 & 92 & 3.0 & 0.52 \\
5  & 1.0 & 90 & 2.8 & 0.47 \\
\hline
\end{longtable}
}

{\small
\begin{longtable}{>{\raggedright\arraybackslash}p{1cm} 
                  >{\centering\arraybackslash}p{2cm} 
                  >{\centering\arraybackslash}p{2cm} 
                  >{\centering\arraybackslash}p{2cm} 
                  >{\centering\arraybackslash}p{1.5cm} 
                  >{\centering\arraybackslash}p{2.0cm}}
\caption{Calibration Phase 2 - Straight Line Test Results}  \label{tab:lineResults} \\
\hline
\textbf{Test No.} & \textbf{Print Speed (mm/s)} & \textbf{Extrusion Speed (mm/s)} & \textbf{Length (mm)} & \textbf{Mean Width (mm)}  & \textbf{Std Dev Width (mm)} \\
\hline
\endhead
\hline
1  & 20 & 0.2 &  93 & 3.0 & 0.27 \\
2  & 20 & 0.3 &  94 & 3.6 & 0.57 \\
3  & 20 & 0.4 &  99 & 4.2 & 0.32 \\
4  & 20 & 0.5 & 101 & 4.5 & 0.34 \\
5  & 25 & 0.2 &  85 & 3.2 & 0.46 \\
6  & 25 & 0.3 &  90 & 3.5 & 0.63 \\
7  & 25 & 0.4 &  94 & 3.8 & 0.26 \\
8  & 25 & 0.5 &  98 & 4.1 & 0.56 \\
9  & 30 & 0.2 &  87 & 2.3 & 0.40 \\
10 & 30 & 0.3 &  97 & 2.9 & 0.46 \\
11 & 30 & 0.4 &  98 & 3.7 & 0.45 \\
12 & 30 & 0.5 &  99 & 4.5 & 0.53 \\
13 & 35 & 0.2 &  92 & 2.2 & 0.53 \\
14 & 35 & 0.3 &  95 & 2.9 & 0.74 \\
15 & 35 & 0.4 &  97 & 3.9 & 0.57 \\
16 & 35 & 0.5 &  98 & 4.1 & 0.79 \\
\hline
\end{longtable}
}

{\small
\begin{longtable}{>{\raggedright\arraybackslash}p{1cm} 
                  >{\centering\arraybackslash}p{2cm} 
                  >{\centering\arraybackslash}p{2cm} 
                  >{\centering\arraybackslash}p{2.5cm} 
                  >{\centering\arraybackslash}p{2.5cm}}
\caption{Calibration Phase 3 - Curved Arc Test Results}  \label{tab:curveResults} \\
\hline
\textbf{Test No.} & \textbf{Radius (mm)} & \textbf{Arc Angle (°)} & \textbf{Mean Width (mm)}  & \textbf{Std Dev Width (mm)} \\
\hline
\endhead
\hline
1  &  5 & 352 & 4.5 & 1.16 \\
2  & 15 & 360 & 4.6 & 0.28 \\
3  & 25 & 357 & 4.7 & 0.27 \\
4  & 35 & 354 & 4.5 & 0.38 \\
5  & 45 & 357 & 4.5 & 0.50 \\
\hline
\end{longtable}
}

{\small
\begin{longtable}{>{\raggedright\arraybackslash}p{1.5cm}
                  >{\centering\arraybackslash}p{2cm}
                  >{\centering\arraybackslash}p{2.5cm}
                  >{\centering\arraybackslash}p{2.5cm}}
\caption{Calibration Phase 6 - Repeatability Test Results}  \label{tab:repeatedResults} \\
\hline
\textbf{Test No.} & \textbf{Length (mm)} & \textbf{Mean Width (mm)}  & \textbf{Std Dev Width (mm)} \\
\hline
\endhead
\hline
1  & 98 & 4.5 & 0.21 \\
2  & 98 & 4.5 & 0.35 \\
3  & 99 & 4.3 & 0.26 \\
4  & 98 & 4.7 & 0.30 \\
5  & 99 & 4.6 & 0.45 \\
\hline
\end{longtable}
}

\section{Visual Record of Printed Samples}
\begin{figure}[H]
    \centering
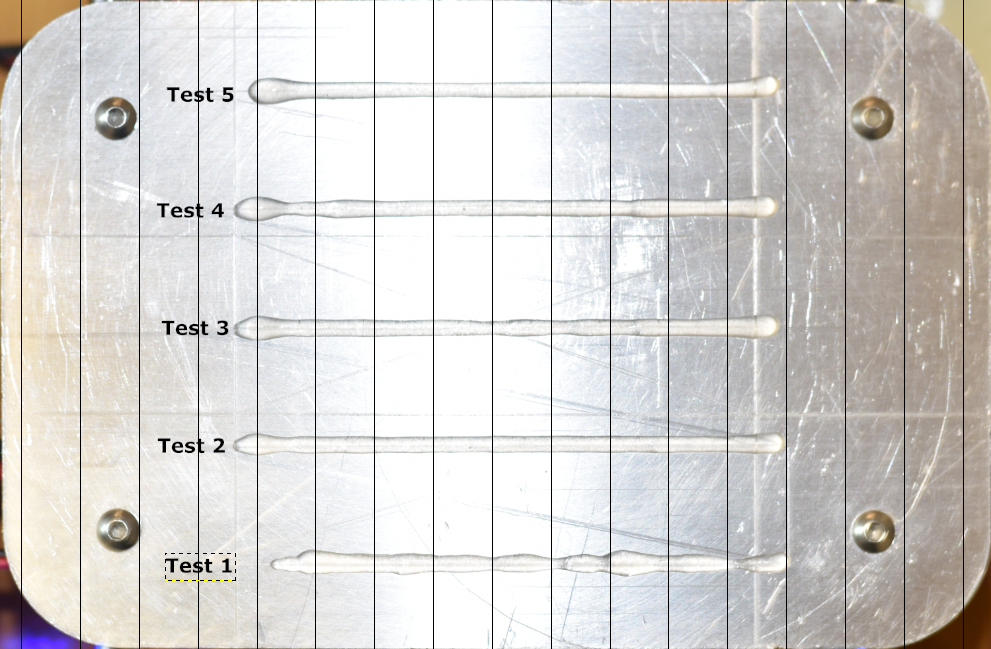
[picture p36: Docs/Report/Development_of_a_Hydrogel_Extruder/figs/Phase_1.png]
    
    \caption{Trial 1 — nozzle height test}
    \label{fig:phase1}
\end{figure}

\begin{figure}[H]
    \centering
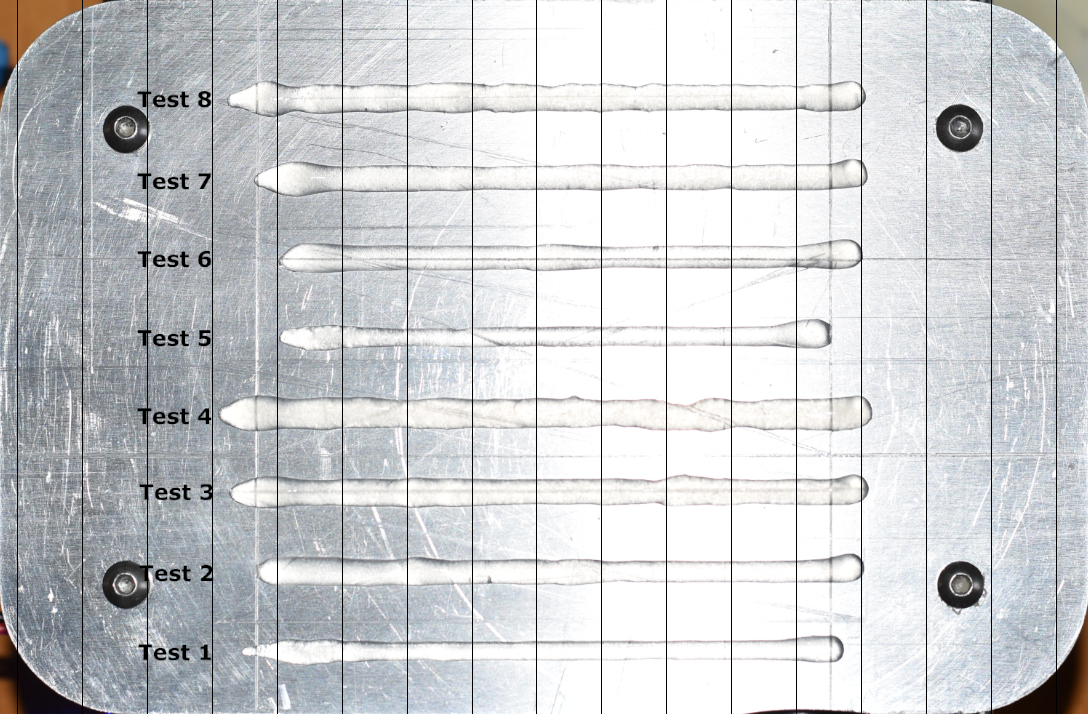
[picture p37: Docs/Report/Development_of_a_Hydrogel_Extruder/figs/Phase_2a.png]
    
    \caption{Trial 2a — straight line test}
    \label{fig:phase2a}
\end{figure}

\begin{figure}[H]
    \centering
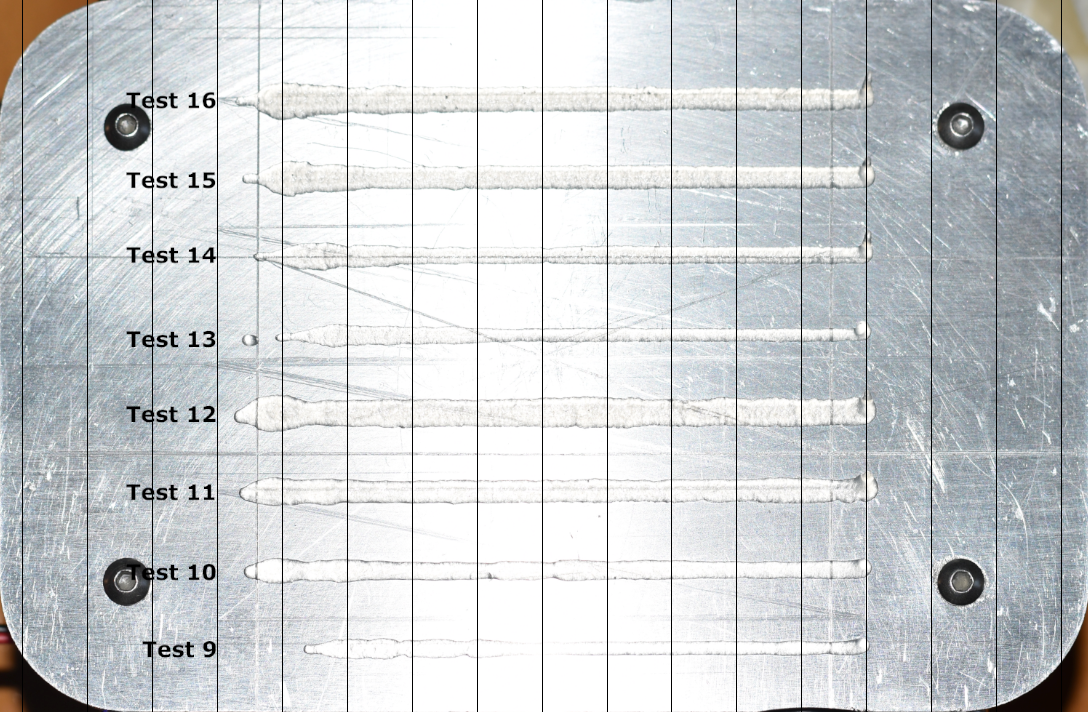
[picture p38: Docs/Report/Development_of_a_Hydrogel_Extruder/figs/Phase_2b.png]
    
    \caption{Trial 2b — straight line test}
    \label{fig:phase2b}
\end{figure}

\begin{figure}[H]
    \centering
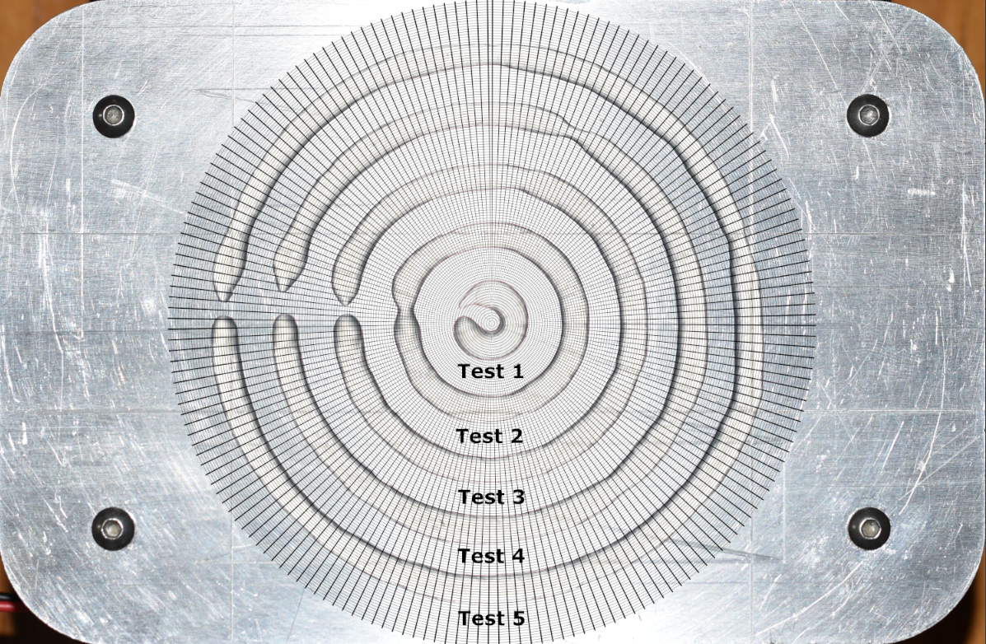
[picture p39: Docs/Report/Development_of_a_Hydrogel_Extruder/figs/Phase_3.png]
    
    \caption{Trial 3 — circle test}
    \label{fig:phase3}
\end{figure}

\begin{figure}[H]
    \centering
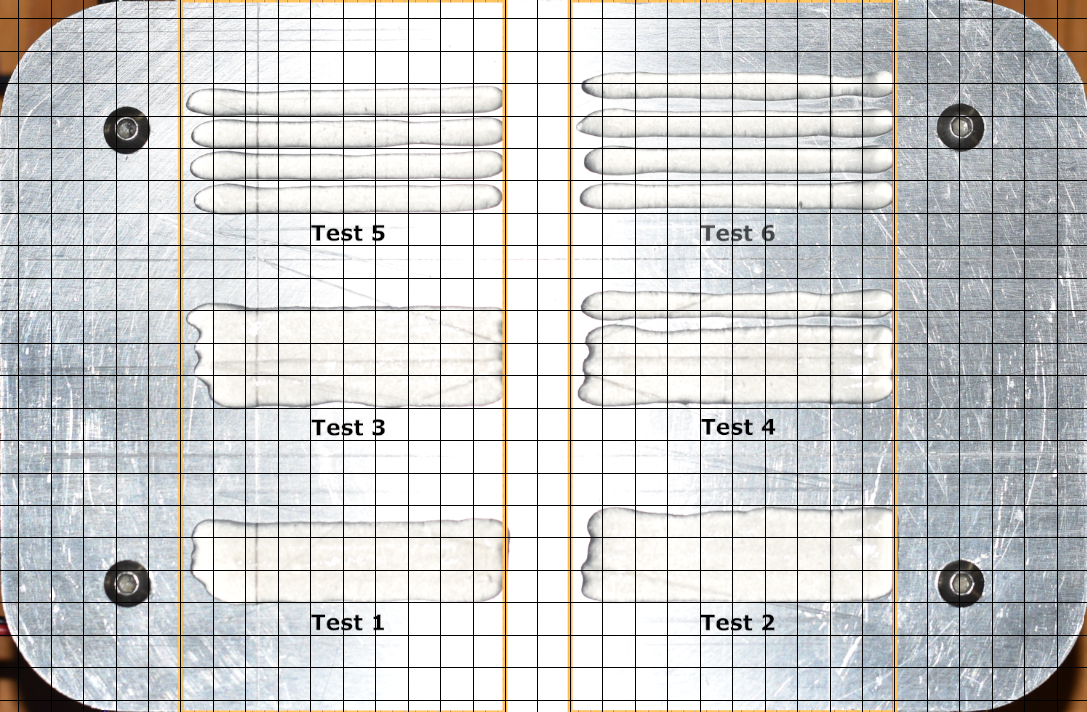
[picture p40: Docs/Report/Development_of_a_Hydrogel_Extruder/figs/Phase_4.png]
    
    \caption{Trial 4 — adjacent lines test}
    \label{fig:phase4}
\end{figure}

\begin{figure}[H]
    \centering
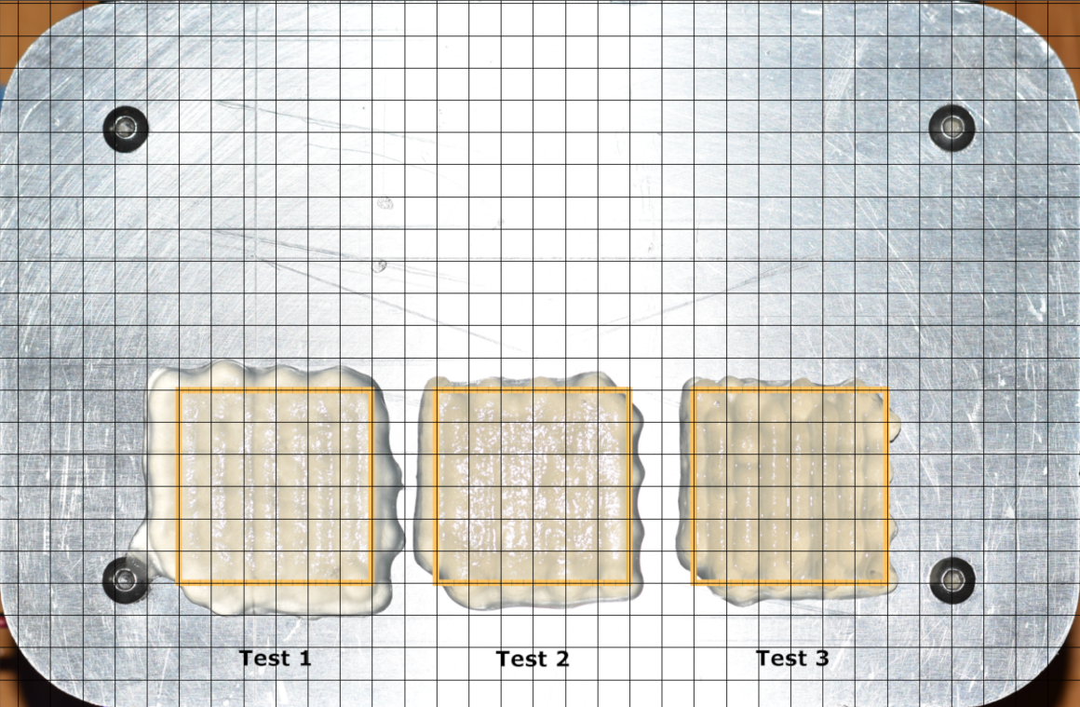
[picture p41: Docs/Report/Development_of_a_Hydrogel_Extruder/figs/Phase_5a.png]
    
    \caption{Trial 5 — stacked layer test}
    \label{fig:phase5a}
\end{figure}
\begin{figure}[H]
    \centering
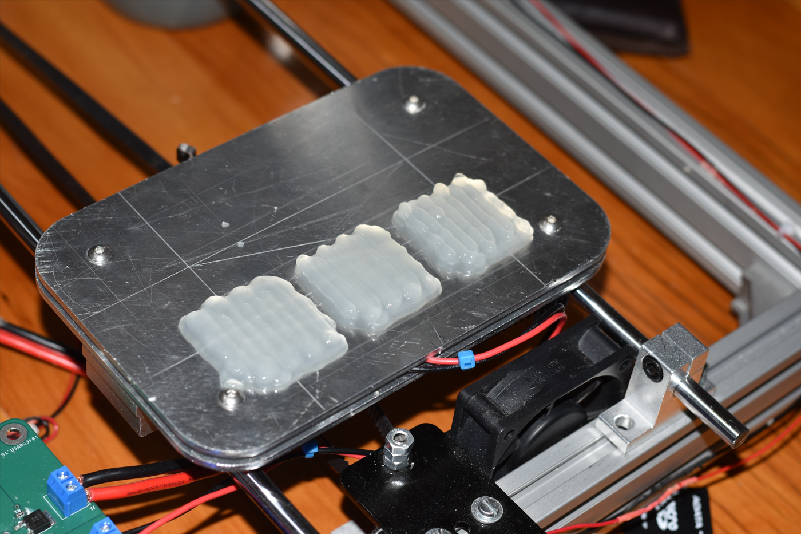
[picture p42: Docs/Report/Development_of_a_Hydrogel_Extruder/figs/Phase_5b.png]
    
    \caption{Trial 5 — angled view}
    \label{fig:phase5b}
\end{figure}

\begin{figure}[H]
    \centering
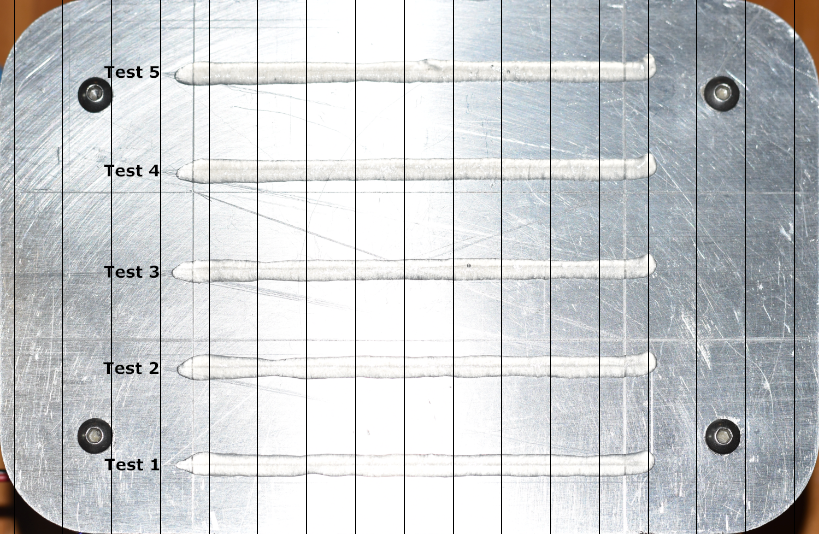
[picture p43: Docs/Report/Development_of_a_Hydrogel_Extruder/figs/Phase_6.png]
    
    \caption{Trial 6 — repeatability test}
    \label{fig:phase6}
\end{figure}

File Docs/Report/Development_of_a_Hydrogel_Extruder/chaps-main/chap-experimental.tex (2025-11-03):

\chapter{Experimental Design}
The purpose of this chapter is to provide an experimental procedure that allows the bioprinter to be calibrated for a specific hydrogel and to ensure user-safety and reliable operation by providing handling and cleaning instructions. 

The printer's purpose is to serve as a research tool for Stellenbosch University’s Physiology Department to characterise unknown bioinks and to fabricate hydrogel scaffolds to model and simulate cell behaviour in biomedical research. To ensure the hydrogel extrusion system is integrated effectively into this research environment, the chapter establishes protocols for adjusting printing parameters to find the optimal settings for different gels, and details procedures to handle the bioprinter and to clean it after use to maintain hygiene and prevent contamination between experiments which ensures cell viability in cases where the printer is used to print cell-seeded structures. The procedure was demonstrated on a surrogate gel for future reference. These guidelines are intended to ensure that the bioprinter can be used consistently, safely, and effectively throughout its utilisation phase.

The calibration procedure involves applying a series of different experiments with the bioprinter and its bioink to optimise its print parameters within different categories of print operations (printing straight, curved, multiple adjacent, and stacked lines). 

\section{Materials and Methods}
\subsection{Materials}
The experimental set-up requires the following equipment and materials:
\begin{itemize}
\item Custom 3D printer with syringe-based extruder
\item HTS Silicone Grease
\item Allen Key
\item Laptop
\item microSD card with microSD card adapter
\item Bioink solution
\item Camera
\item Calliper
\end{itemize}

\noindent For the surrogate gel, the following equipment and materials are required:
\begin{itemize}
\item Store-bought Agar powder 
\item Kettle
\item Measurement jug
\item Measurement spoons (1 tsp, 1/2 tsp)
\end{itemize}

\begin{figure}[H]
    \centering
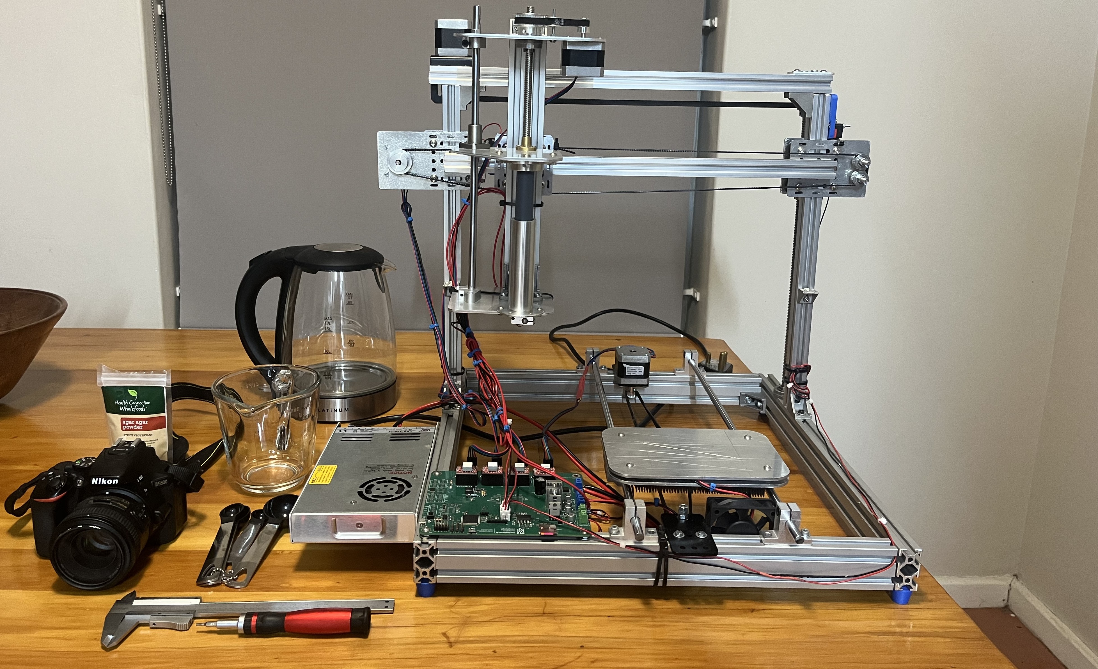
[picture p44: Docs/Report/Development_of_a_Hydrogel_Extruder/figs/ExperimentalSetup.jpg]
    
    \caption{Experimental Set-up}
    \label{fig:experimentalSetup}
\end{figure}

 \begin{figure}[H]
    \centering
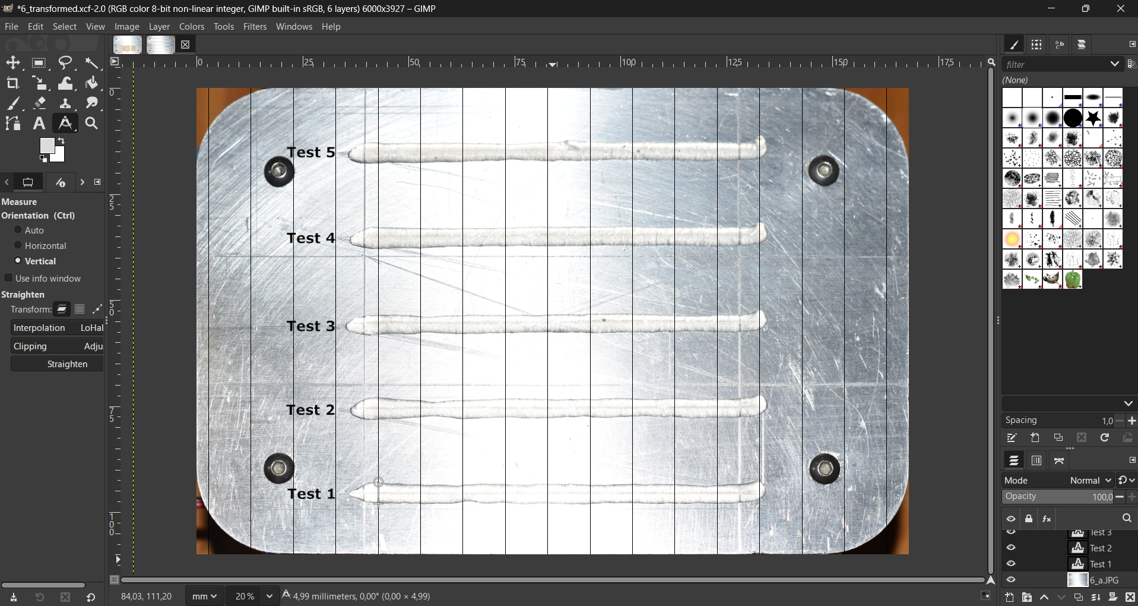
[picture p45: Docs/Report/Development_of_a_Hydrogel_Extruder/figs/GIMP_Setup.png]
    
    \caption{GIMP Set-up}
    \label{fig:GIMPSetup}
\end{figure}

The bioprinter is comprised of an extruder and a gantry. The extruder uses a lead screw to extrude the gel out of a custom syringe onto a cooled aluminium bed. The extruder position relative to the printer frame, is varied across 3D space by a gantry that uses belts to adjust the extruder position in the horizontal plain and uses a lead screw to adjust the nozzle height.

The bioprinter's print instructions are loaded via a microSD card which is inserted into and read by the bioprinter to perform each calibration trial. The laptop is also used to read transmitted USB information which is read in Termite. 

After each print iteration, a photo is taken of the print bed and its dimensions are analysed using GIMP (Figure~\ref{fig:GIMPSetup}) to assess the print quality. This experimental set-up is shown in Figure~\ref{fig:experimentalSetup}.

\subsection{Equipment Specifications}
The experimental equipment must allow multiple strands of hydrogel to be extruded onto a printing surface where the line’s width can be measured at points along the line without distorting the line’s dimensions during the measurement process. 

\subsubsection*{Gel Specifications}
The gel specifications depend on the research needs of the end-user, with each hydrogel type and concentration coming with its own rheological properties and storage and handling protocols.

This experimental procedure, however, was applied to a surrogate gel that is an agar-water mixture. Store-bought Agar-agar powder is dissolved in water at 4.5\% w/v. Agar powder was used as it is easy to prepare and gels more rapidly when cooled compared to other store-bought alternatives such as gelatin. Agar is a suitable surrogate for GelMA as they are both thermally reversible and shear-thinning hydrogels whose viscosities that decrease with increasing temperature and solidify upon cooling, making agar a low-cost substitute for testing.

\subsubsection*{Bioprinter Specifications}
\begin{itemize}
    \item \textbf{Extruder} – This consists of a 25~ml syringe with a nozzle diameter of 1.0\,mm. The nozzle heater block is capable of reaching a maximum temperature of 230 $^{\circ}$C.
    
    \item \textbf{Gantry} – The gantry is used to position the extruder in 3D space. Two NEMA 17 stepper motors drive belts that control the 2-axis motion in the horizontal plane. A lead screw (also driven by a NEMA 17) with an 8\,mm lead is used to control the extruder’s vertical position.
    
    \item \textbf{Bed} – The gel is printed on a 110\,mm $\times$ 168\,mm aluminium bed. The bed is capable of reaching a minimum temperature of 13 $^{\circ}$C.
\end{itemize}
\subsubsection*{Camera Specifications}
Print sample photos are taken using a Nikon D5600 (DSLR) with an AF-S NIKKOR 50~mm f/1.8G SWM aspherical $\phi58$ lens. The camera operates in aperture priority mode with flash enabled, an aperture of f/4.5, and an image resolution of 6000 × 4000 pixels. Photographs are taken by hand under ambient lighting conditions.

\subsubsection*{Software}
\begin{itemize}
    \item \textbf{GIMP} – This is used to distort the image to remove the angled perspective effect that varies between hand operated camera shots and measure the dimensions of the print strands for each print trial.
    \item \textbf{MATLAB} – The measured data from the printing trials are stored manually and processed in MATLAB using the \texttt{Trial\_Processing.m} file in the project’s \href{https://github.com/SimonDaniel605/Hydrogel-3D-Printer/tree/main/Experiments}{GitHub repository's \texttt{Experiments} folder} \citep{Daniel2025_HydrogelPrinter}.
\end{itemize}

\subsection{Methods}

The variables identified, relating to the calibration procedure, are shown below in Table~\ref{tab:variables}:

\begin{longtable}{>{\raggedright\arraybackslash}p{4cm} p{10cm}}
\caption{Experimental Variables} \label{tab:variables}\\
\hline
\textbf{Variable Type} & \textbf{Variables} \\
\hline
Independent Variables & Extrusion rate, print speed, bed-nozzle height, print arc radius, line spacing \\
Dependent Variables   & Layer width, layer height, print stability \\
Controlled Variables  & Gel concentration, print line length, nozzle diameter \\
Extraneous Variables  & Ambient temperature, vibrations, gel rheological properties \\
\hline
\end{longtable}

During the analysis of results, the mean line width, the standard deviation of the line width (each in mm) along with the overall quality of each print trial is analysed and compared against the varied printing parameters: extrusion rate (mm/s), printing speed (mm/s), bed-nozzle height (mm), print circle radius (mm), horizontal line spacing (mm), and nozzle height increment (mm). The standard deviations serve as measures of print stability (by indicating consistent width), where high deviations indicate lower print stability and quality. Because the rate at which the ink gets extruded depends on the nozzle diameter, extrusion rate (in this chapter only) is defined as the speed (in mm/s) at which the plunger moves through the syringe.

The controlled variables in the experiment are the nozzle diameter and gel concentration. The nozzle diameter influences the width of deposited strands and is therefore kept constant across all trials. The gel concentration affects the fluid behaviour of the solution and is held constant to minimise variations in flow properties between print tasks.

Ambient temperature and environmental vibrations, including those from the printer itself, can also influence outcomes. However, these are considered extraneous variables and are not within the scope of control in this experiment. Since the printer is intended to characterise unknown gels, the gel's rheological behaviour, even under constant concentration, is considered as an extraneous variable.

\subsubsection*{Gel preparation}

The following steps detail how to prepare the agar surrogate gel.

\begin{enumerate}
    \item Fill the kettle with water and heat water until boiling ($100~^{\circ}$C).
    \item From the kettle, pour the boiling water into a clean measurement jug until the bottom of the meniscus reaches the 100\,mL mark on the measuring jug.
    \item Using the measuring spoons, add 1.5 teaspoons (4.5~g) of agar powder to the measurement jug. 
    \item Mix the solution until homogeneous, and continue stirring every 10 minutes until an hour has passed since the solution was first stirred. 
    \item After the first stir, complete steps 1 to 4 of the experimental set-up procedure.
\end{enumerate}

\subsubsection*{Experimental Set-up Procedure}
Before the calibration, the a set-up procedure must first be conducted. 
\begin{enumerate}
    \item Plug the printer’s three-prong power plug into a standard power socket. The PCB indicator light should turn green, the gantry will home, and the bed cooling system will activate.
    \item Using the laptop, load the print settings and print tasks (according to the needs of the specific experimental trial that is being conducted) onto the microSD card.
    \item Using the Allen Key, unbolt the syringe from the extruder assembly and unscrew the syringe from the hot-end assembly.
    \item Check and ensure syringe is clean and press the plunger until it is fully depressed to the bottom of the syringe tube.
    \item Once the gel solution is ready for use, submerge the tip of the syringe into the substance and pull the plunger until it reaches the end of the syringe or a sufficient volume of the solution is extracted.
    \item Once the printer fluid has been loaded, wipe the syringe sections that were submerged during extraction with a cloth.
    \item Screw the hot-end assembly back on to the threaded syringe tip and mount the flanged syringe back onto the extruder platform using the bolts and Allen Key (make sure at least two bolts are fastened along the flange mounting holes.
    \item Insert the card into the bioprinter circuit board's microSD port, and press the reset button to begin printing.
    \item Do not touch the printer during operation and keep the area around moving parts and nip points clear of loose items.
    \item Once the print trial is done, use the camera to take a overhead photo of the print bed.
    \item Analyse the results in GIMP.
    \item Perform clean-up procedure.
\end{enumerate}

\subsubsection*{Cleaning Procedure}
To clean the bioprinter after use the following steps are taken:
\begin{itemize}
    \item Make sure the printer is disconnected from its power source, and wait for the circuit board's green light to completely turn off.
    \item With a cloth, remove any prints from the printer bed and wipe the platform.
    \item Use the Allen key to remove the syringe from the extruder platform.
    \item Unscrew both the nozzle and syringe from the heater block.
    \item Remove the plunger and pour any residual unsolidified liquid into a sink.
    \item Rinse both the syringe and nozzle with warm water.
    \item Fill the syringe with water and use the plunger to push it out to ensure there is no clogging.
    \item Leave the syringe, nozzle, and plunger to dry.
    \item Once dry apply a fresh coat of HTS silicone grease to the plunger head before reassembling the extruder.
\end{itemize}
\subsubsection*{GIMP Processing}
Once the photos are taken, they must be processed and analysed in GIMP. 
\begin{itemize}
    \item Using the transformed tools scale the image to 6000x3928 to match the bed dimension's ratios.
    \item Then use the perspective tool and drag the bed edges to precisely align the demarcated rectangle.
    \item Go to \texttt{Scale Image} in the \texttt{Image} tab and set the X and Y pixels per mm to 35.7 and the image size should precisely match the bed dimensions of 168x110 mm.
    \item Show a grid using \texttt{View} and then using \texttt{Configure Grid} in the \texttt{Image} tab, create horizontal spacings of 10~mm to ensure line widths are equally spaced, create vertical spacings of 0.1~mm to ensure 0.1~mm measurement accuracy, and offset the grid horizontally by 153.6~mm to ensure the vertical grid-lines align with the etched bed centre.
    \item Using the measuring tool, measure the required line widths and manually store the results in the \texttt{Trial\_Processing.m} file in the project’s \href{https://github.com/SimonDaniel605/Hydrogel-3D-Printer/tree/main/Experiments}{GitHub repository's \texttt{Experiments} folder} \citep{Daniel2025_HydrogelPrinter}.
\end{itemize}
\subsubsection*{Nozzle Height Test}
Once the setup is complete, the calibrations can begin. 6 different printing phases are conducted with each phase using its own PrintTask.csv file. These CSV files, along with the MATLAB scripts that generated them, can also be found in the \texttt{Experiments} folder of the project repository \citep{Daniel2025_HydrogelPrinter}. Each print task is repeated multiple times, and the trials exhibiting the fewest instances of temporary clogging or entrapped air bubbles (identified by random gaps along deposited strands) are included in the appendices (the rest are shown in the GitHub repository for transparency). This approach ensure the independent variable is the only factor influencing the dependant variables.  A description of the print plan of the nozzle height test can be seen below.

\begin{enumerate}
    \item The first experiment is to determine the optimal vertical nozzle height to print straight lines. 5 adjacent 100 mm straight lines are printed on the bed with a gantry speed of 20~mm/s and extrusion rate of 0.2 mm/s with 5 different nozzle offsets as in the proposed test matrix in Table~\ref{tab:heightmatrix}. This task is repeated 5 times.
    \item The width of the 100 mm lines are measured at 11 equi-spaced points and the mean and standard deviation of these widths for each line are calculated.
    \item The results are evaluated in the Discussion of Results section to determine the optimal height value, which is then used to print the lines in the next calibration phase.
\end{enumerate}

\subsubsection*{Speed Test}
\begin{enumerate}
    \item The second experiment determines the optimal print speed and extrusion rate. 16 straight lines (100 mm long) are printed across two print tasks with varying extrusion rates for different print speeds according to Table~\ref{tab:linetestmatrix}. This task is repeated 5 times.
    \item The width of the 100 mm lines are measured at 11 equi-spaced points and the mean and standard deviation of these widths for each line are calculated.
    \item The results are evaluated in the Discussion of Results section to determine the optimal height value, which is then used to print the lines in the next calibration phases.
\end{enumerate}

\subsubsection*{Curved Arc Test}
\begin{enumerate}
    \item The third experiment determines the optimal centripetal acceleration used to print a curved line. It does so by printing 5 concentric circles with differing radii according to the proposed test matrix in Table~\ref{tab:curvetestmatrix}. The previously determined print settings are used including tangential print speed which is held constant to ensure that the centripetal acceleration is differing due to the change in radius ($a_c=\frac{v^2}{r}$). This task is repeated 5 times.
    \item The width of each circle's lines will be measured at 12 equi-spaced points (every $30^\circ$), and the mean and standard deviation of these widths for each circle are calculated, analysed, and evaluated in the Discussion of Results section.
\end{enumerate}

\subsubsection*{Adjacent Line Test}
\begin{enumerate}
    \item The goal of the fourth experiment is to determine the optimal horizontal spacing with which the nozzle is offset by when printing horizontal rectangles. It does so by printing 6 sets of 4 adjacent 50 mm lines, with each set varying in how much the nozzle is horizontally offset (proposed offsets in Table~\ref{tab:spacingmatrix}). The print settings determined from previous calibration stages are used and held constant between each rectangle speed. This task is repeated 5 times.
    \item The results are process in GIMP and qualitatively analysed in the results section to determine the maximum line spacing trial that never forms gaps between  adjacent strands.
    \item The optimal line spacing is used to print the next calibration task.
\end{enumerate}

\subsubsection*{Layer Stacking Test Procedure}
\begin{enumerate}
    \item The goal of the fifth experiment is to determine the optimal vertical nozzle height increase between successive scaffold layers. This is achieved by printing three 4 layer prisms with a target base of 30x30 mm, each with a different height increment (Table~\ref{tab:stackingmatrix}). The previously determined optimal print settings are used and held constant across each cuboid. This is repeated 4 times.
    \item An overhead photograph is still taken for this trial to be processed in GIMP and an additional angled photograph is captured to illustrate the 3D nature of the print.
    \item The calliper's depth rod is used to determine the overall scaffold height by inserting it until it contacts the bed surface, then sliding the calliper body down until its end aligns with the top of the printed structure. The calliper is kept vertical throughout this process.
    \item The results are analysed to identify the vertical offset that produces the best print quality.
\end{enumerate}
\subsubsection*{Repeatability Test Procedure}
\begin{enumerate}
    \item To determine the repeatability of the printer with its optimised print settings, a sixth trial is conducted using the nozzle offset, extrusion rate, and print speed from Trials 1 and 2. Five 100~mm lines are printed on the bed. This is repeated three times. 
    \item The width of the 100 mm lines are measured at 11 equi-spaced points and the mean and standard deviation of these widths for each line are calculated.
    \item The results are evaluated in the Discussion of Results section to assess the repeatability of the printer's performance.
\end{enumerate}

\section{Discussion of Results and Conclusion}
\subsection*{Trial 1 - Nozzle Height Test}
The processed image of the first printing trial is shown in Figure~\ref{fig:phase1}, and the corresponding measurements obtained in GIMP and further processed in MATLAB are summarised in Table~\ref{tab:heightResults}. 

The nozzle height that produced the line with the most consistent width and a printed length closest to the 100~mm target was 0.4~mm. Consequently, all subsequent print trials were performed with a first-layer nozzle offset of 0.4~mm.

The line printed at the smallest offset (0.2 mm) was noticeably shorter. This is likely because the minimal gap maximised the contact area between the nozzle and the gel, thereby increasing the adhesive forces at the nozzle tip. As a result, the initial portion of the extruded strand tended to follow the nozzle for a brief period before settling, yielding a shorter printed strand.

To assess whether the independent variable -- the nozzle height -- exhibited any meaningful correlation with the measured line properties, correlation coefficients were calculated in MATLAB. The correlation between nozzle height and line length, mean width, and width standard deviation was 0.131, -0.333, and -0.330. These weak correlations indicate that nozzle height did not have a strong influence on the printed line length, width, or variability. Since no statistical relationship was found between nozzle height and print quality, the 0.4~mm offset was selected as a reasonable baseline for the subsequent calibration phases.

\subsection*{Trial 2 - Speed Test}
Figures~\ref{fig:phase2a} and~\ref{fig:phase2b} show the processed images of the speed printing trial, in which print speed and extrusion rate were varied to evaluate their combined influence on line quality. The corresponding results are tabulated in Table~\ref{tab:lineResults}, and the correlation analysis is shown in Table~\ref{tab:phase2corr}. 

The plots in Figure~\ref{fig:mplots} illustrate the relationships between the line characteristics and extrusion rate at each print speed. These figures show that increasing the extrusion rate produces a consistent rise in mean line width for all speeds, each exhibiting a clear linear relationship. This trend matches the expected behaviour, as a higher extrusion rate increases the volumetric flow of gel through the nozzle, thereby depositing more gel per unit time (when print speed is kept constant) and resulting in wider lines. This is further corroborated by the correlations in Table~\ref{tab:phase2corr} which show a strong positive correlation ($r = 0.97$–$1.00$).

The plots and correlation analysis show a strong relationship between line length and extrusion rate ($r = 0.86$–$1.00$). Lines printed at higher extrusion rates were longer and more closely matched the 100~mm target length. This occurs because faster extrusion establishes the gel flow sooner, allowing the gel to contact and adhere to the bed closer to the intended start. At lower extrusion rates, the nozzle travels further before the delayed flow can achieve gel deposition, resulting in a shorter line.

The effect of extrusion rate on the line width variation differed between print speeds. At print speeds between 20 and 25 mm/s, no correlation was found ($r \approx0$), indicating that increasing extrusion rate at low speeds does not affect print line width stability. When print speed increased to between 30 and 35 mm/s, the correlation became strongly positive, showing that higher extrusion rates at elevated speeds increased the likelihood of irregularities forming along the line.

These results show that lines printed with lower print speeds and higher extrusion rates result in the most uniform and repeatable lines that more closely match the target line length. Based on this trend, a print speed of 20~mm/s and an extrusion rate of 0.4~mm/s were selected for the rest of the calibration process, as this setting yielded the most favourable combination of line width stability (with a mean of 4.2~mm) and length (99~mm).

\begin{figure}[H]
    \centering
    \begin{subfigure}[t]{0.49\textwidth}
        \centering
        
        \caption{Length}
        \label{fig:Lgraph}
    \end{subfigure}
    \hfill
    \begin{subfigure}[t]{0.49\textwidth}
        \centering
        
        \caption{Mean Width}
        \label{fig:Wgraph}
    \end{subfigure}
    \hfill
    \begin{subfigure}[t]{0.55\textwidth}
        \centering
        
        \caption{Width Standard Deviation}
        \label{fig:Sgraph}
    \end{subfigure}
    \caption{Graphs showing the relationship between line characteristics and extrusion rate}
    \label{fig:mplots}
\end{figure}
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

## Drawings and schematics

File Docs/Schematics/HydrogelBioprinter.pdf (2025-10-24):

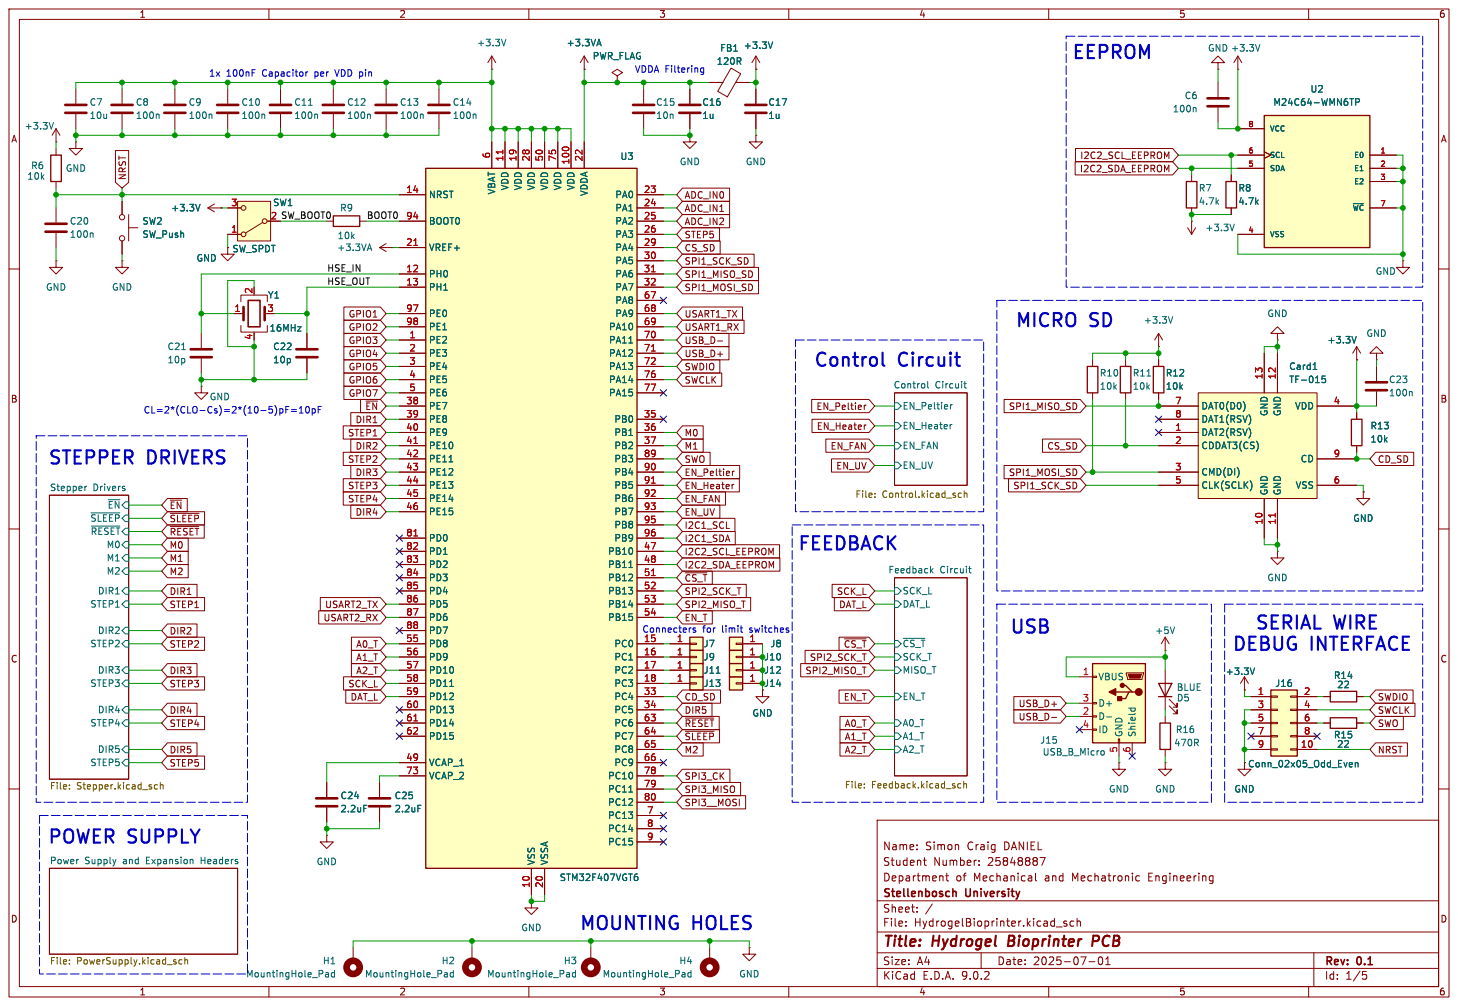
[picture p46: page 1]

6 VDD 11 VDD 19 VDD 28 VSS 10 VDD 50 VSSA 20 VDD 75 VDD 100 VDDA 22 PA0 23 PA1 24 PA2 25 PA3 26 PA4 29 PA5 30 PA6 31 PA7 32 PA8 67 PA9 68 PA10 69 PA11 70 PA12 71 PA13 72 PA14 76 PA15 77 PB0 35 PB1 36 PB2 37 PB3 89 PB4 90 PB5 91 PB6 92 PB7 93 PB8 95 PB9 96 PB10 47 PB11 48 PB12 51 PB13 52 PB14 53 PB15 54 PC0 15 PC1 16 PC2 17 PC3 18 PC4 33 PC5 34 PC6 63 PC7 64 PC8 65 PC9 66 PC10 78 PC11 79 PC12 80 PC13 7 PC14 8 PC15 9

CL=2*(CLO-Cs)=2*(10-5)pF=10pF

~{CS_T} SCK_L Feedback Circuit File: Feedback.kicad_sch

Id: 1/5 Title: Hydrogel Bioprinter PCB

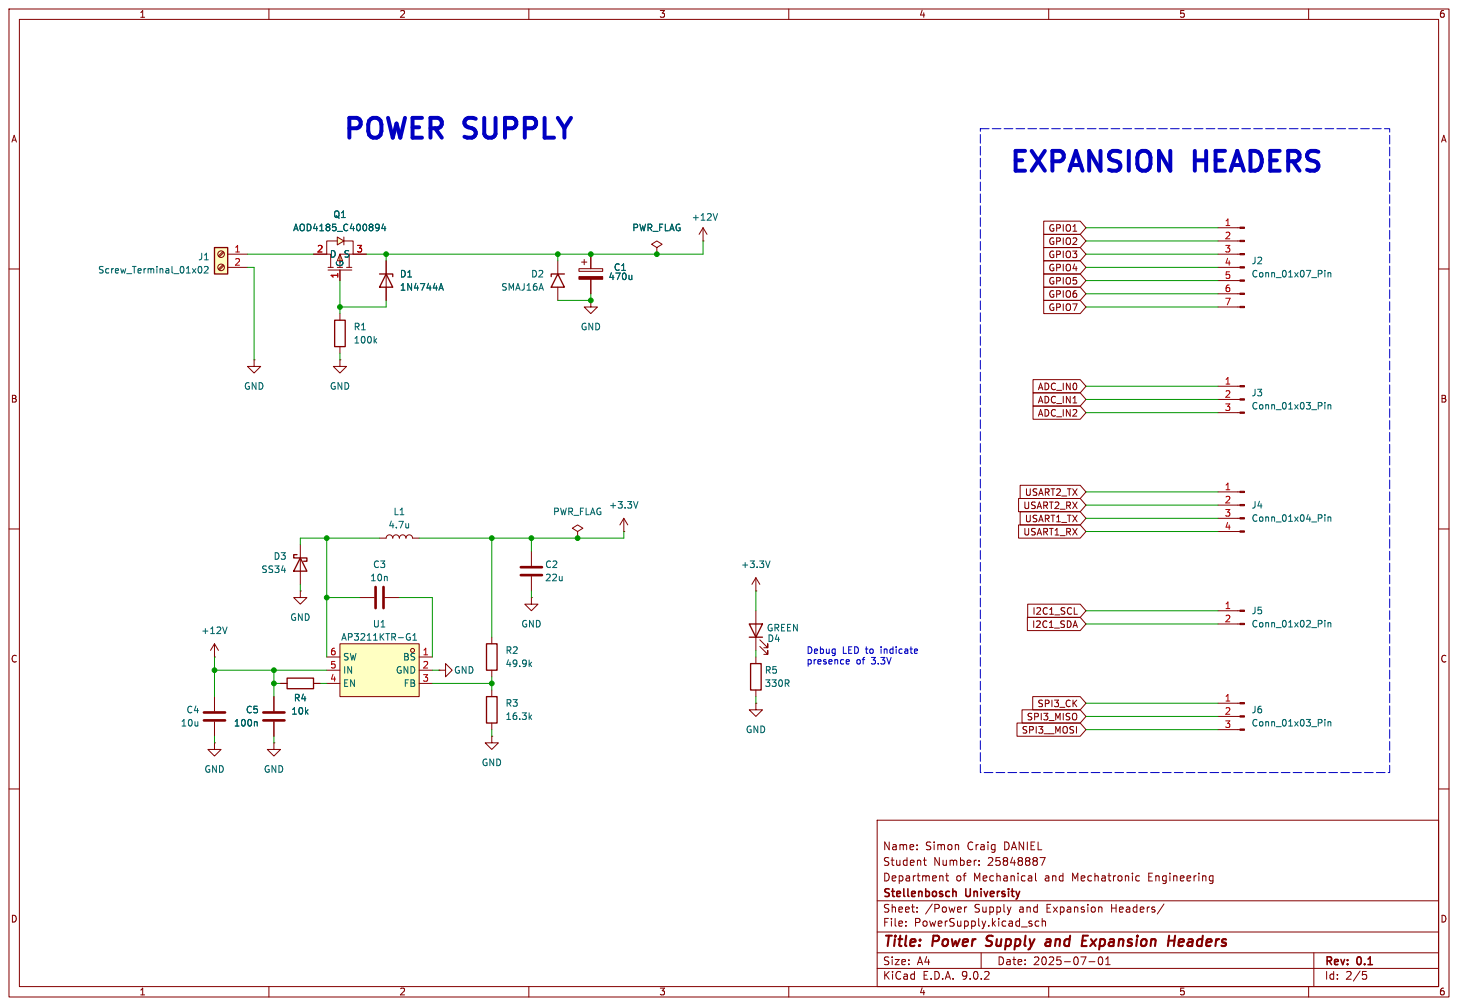
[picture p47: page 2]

presence of 3.3V POWER SUPPLY

SPI3__MOSI SPI3_CK GPIO1 GPIO4 GPIO2 USART1_TX GPIO5 GPIO7 GPIO6 GPIO3 Debug LED to indicate

Id: 2/5 Title: Power Supply and Expansion Headers

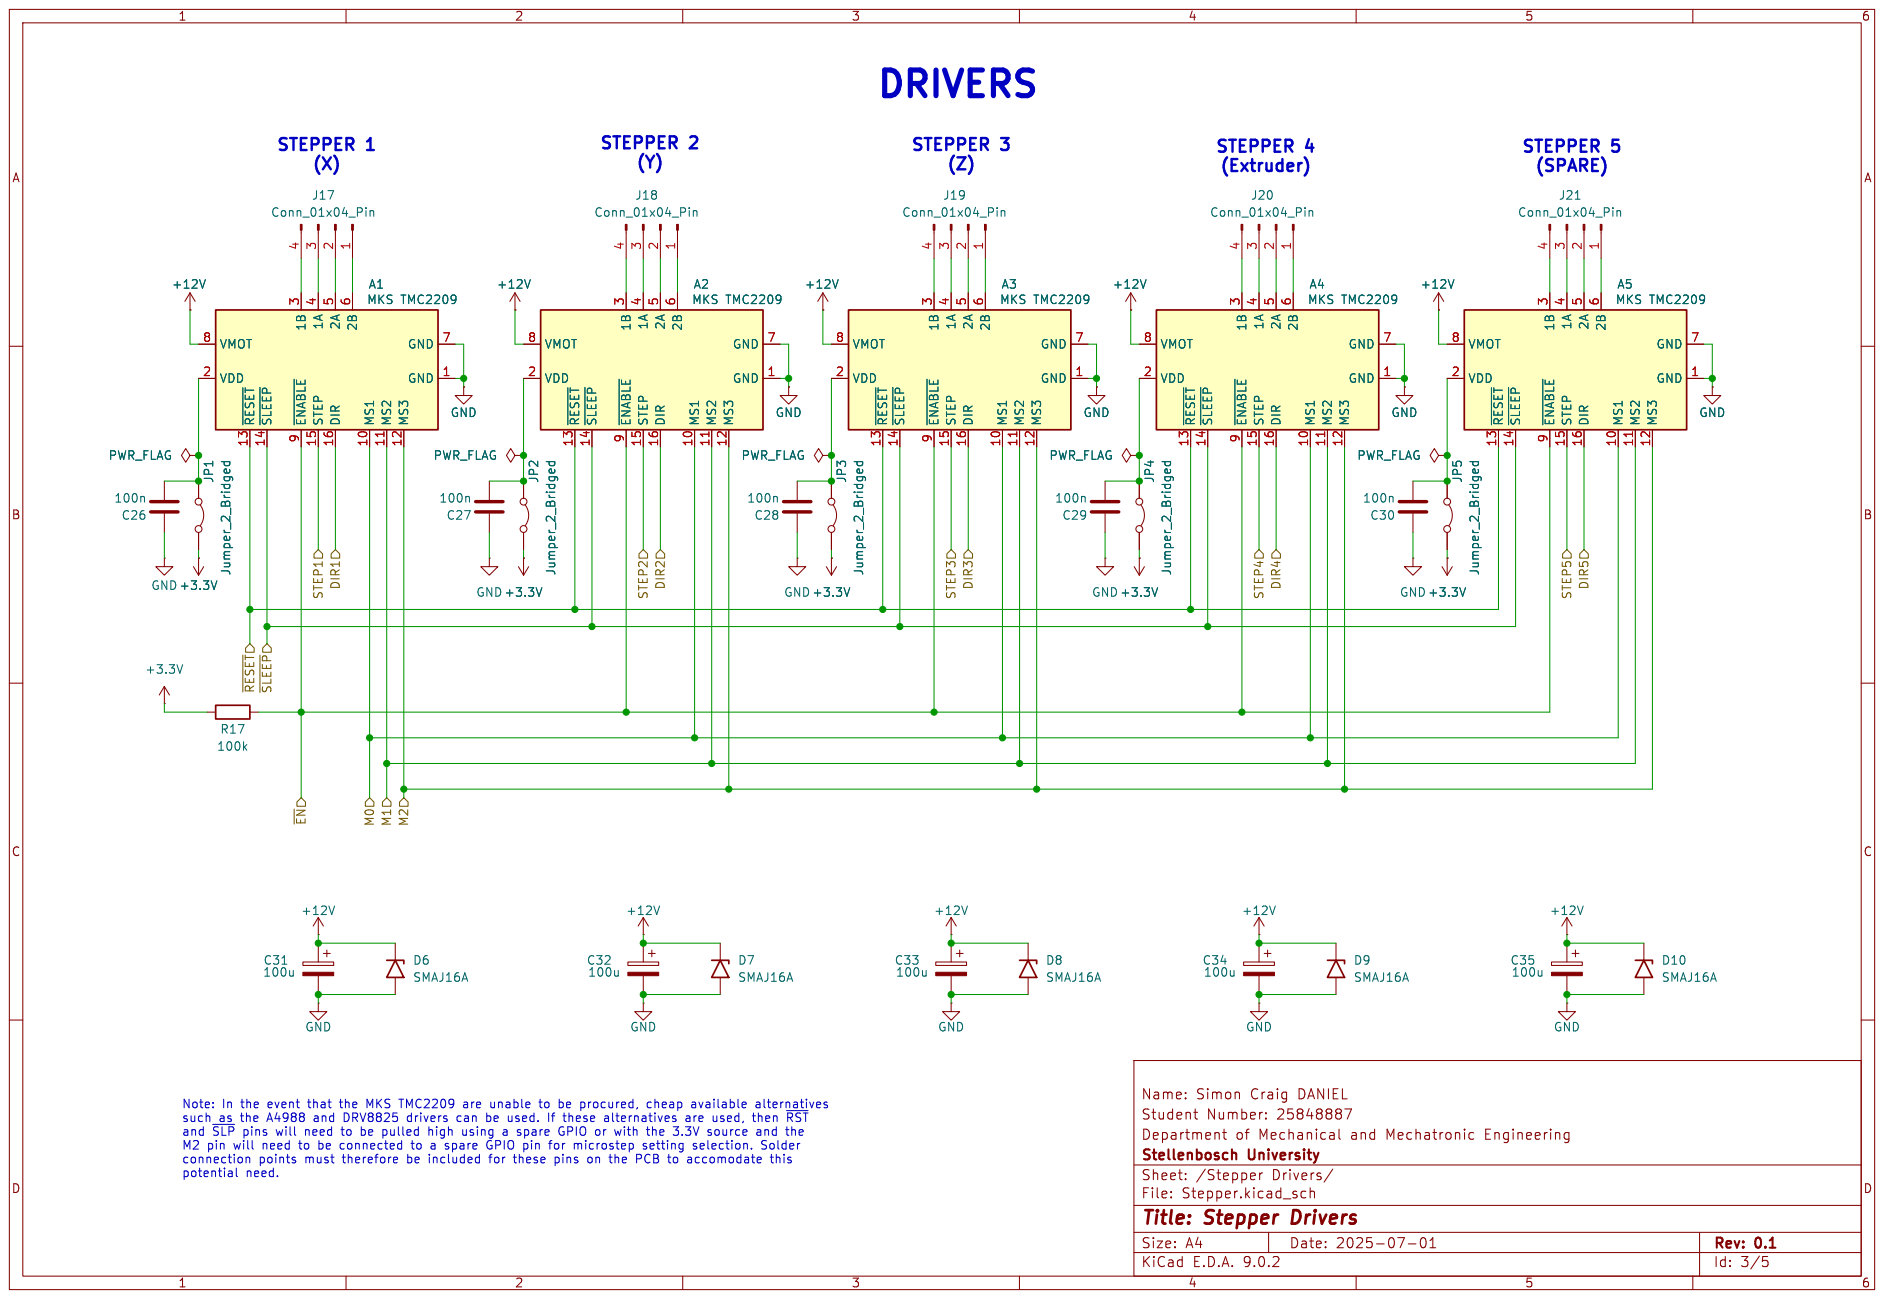
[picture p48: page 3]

Id: 3/5 Title: Stepper Drivers

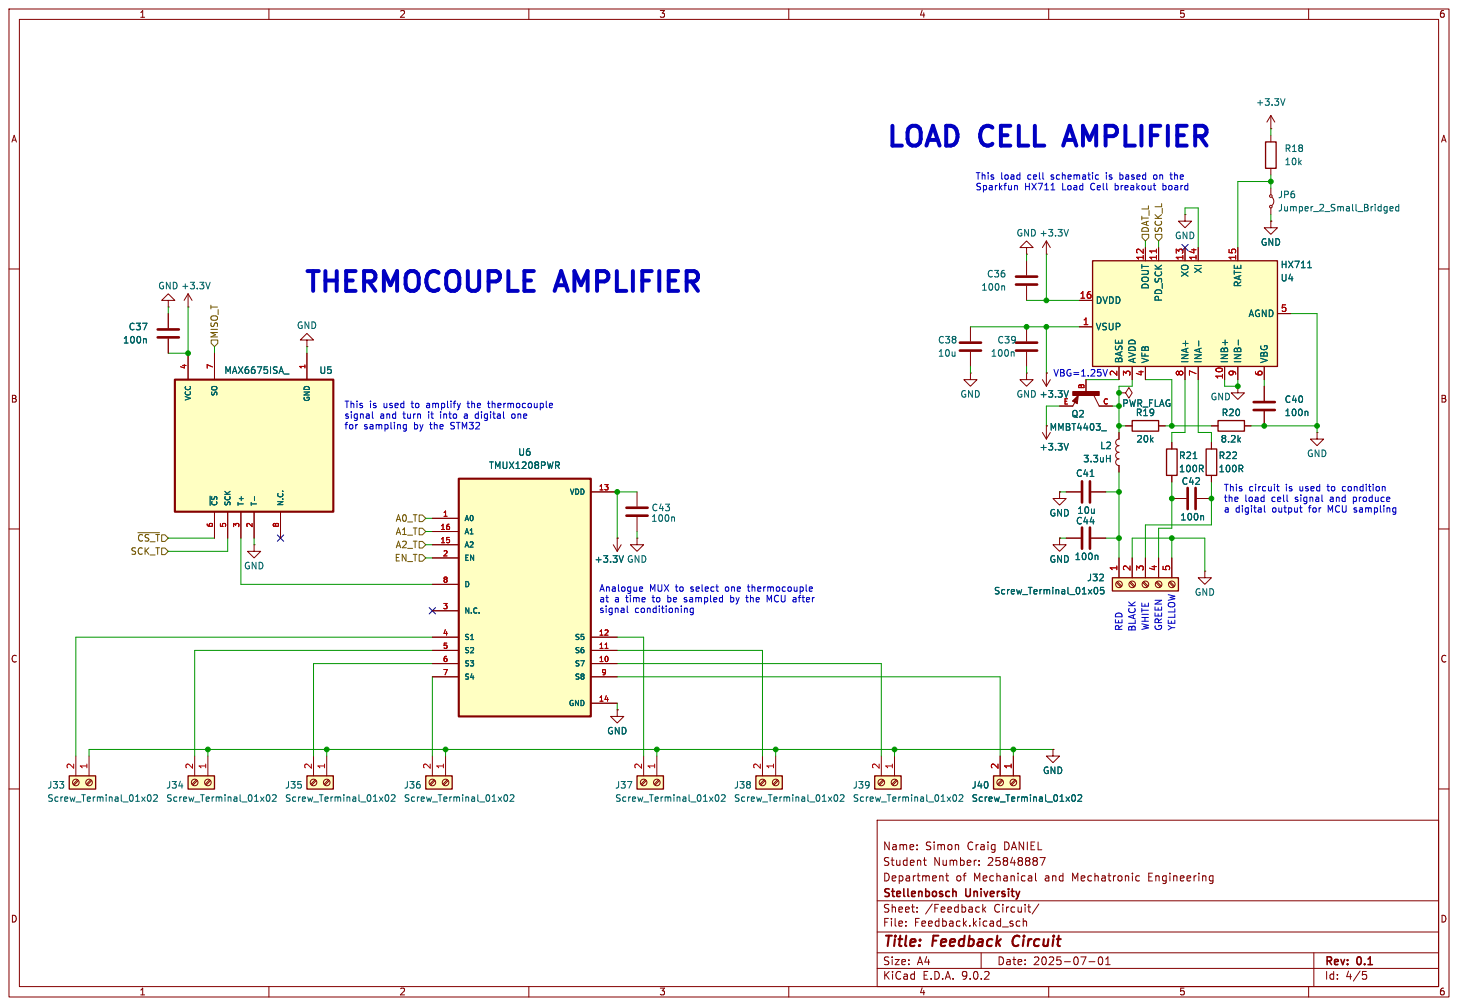
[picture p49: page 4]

6 VSUP 1 AGND 5 DVDD 16 DOUT 12 PD_SCK 11 XO 13 XI 14 RATE 15 U4 HX711 GND GND

6 VSUP 1 AGND 5 DVDD 16 DOUT 12 PD_SCK 11 XO 13 XI 14 RATE 15 R20

8 INA- 7 INB+ 10 INB- 9 VBG

the load cell signal and produce

Analogue MUX to select one thermocouple

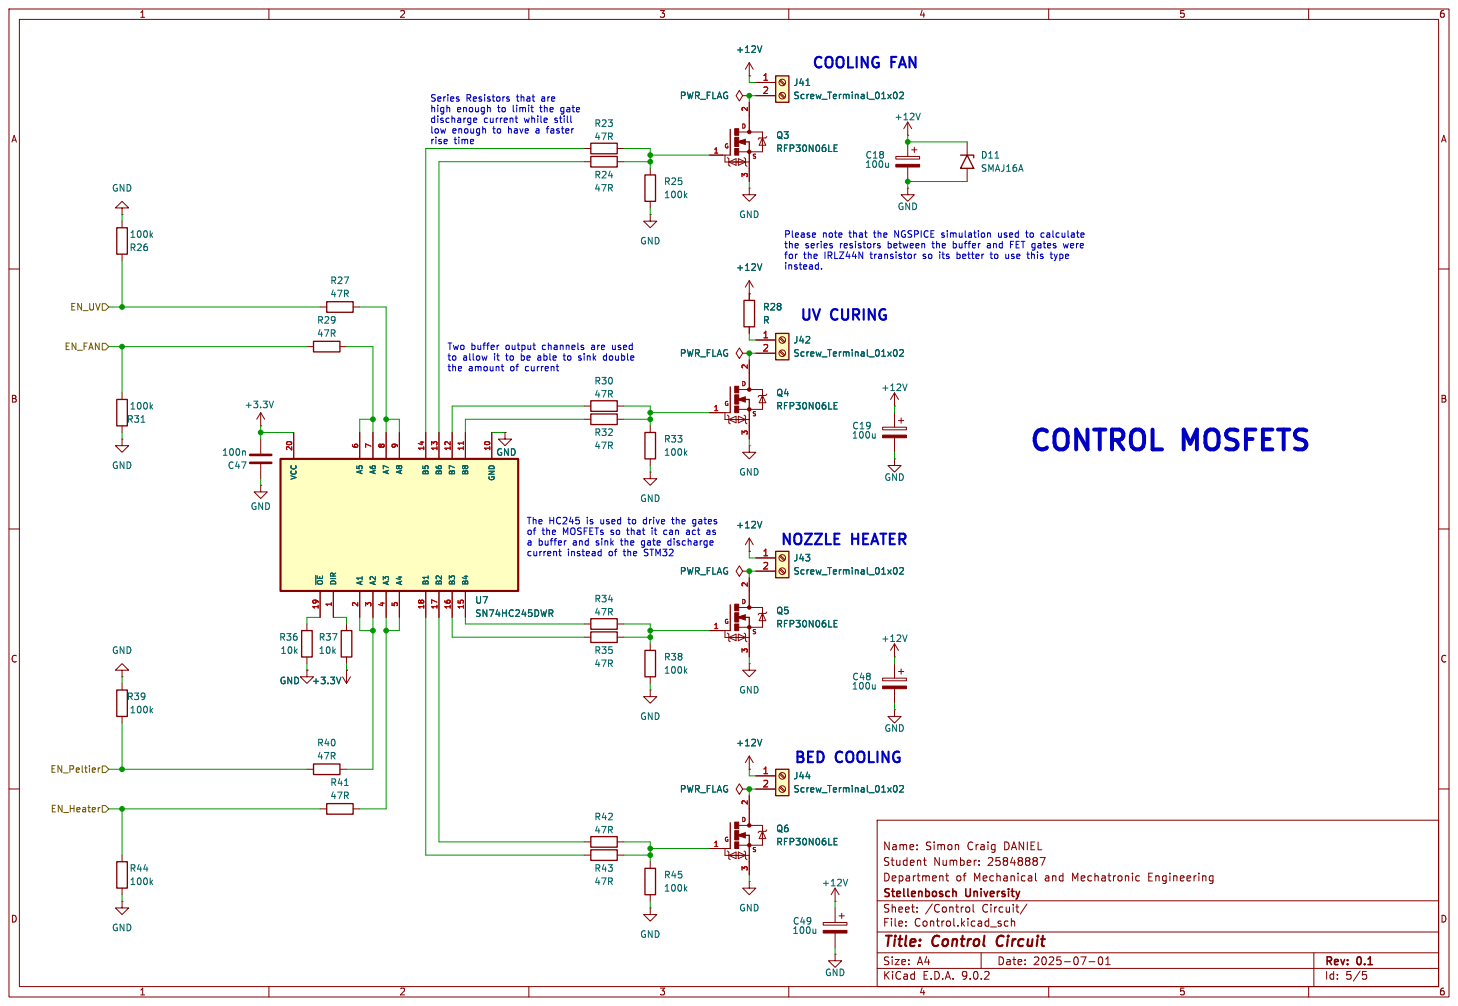
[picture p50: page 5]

high enough to limit the gate
low enough to have a faster
rise time

to allow it to be able to sink double

The HC245 is used to drive the gates of the MOSFETs so that it can act as a buffer and sink the gate discharge

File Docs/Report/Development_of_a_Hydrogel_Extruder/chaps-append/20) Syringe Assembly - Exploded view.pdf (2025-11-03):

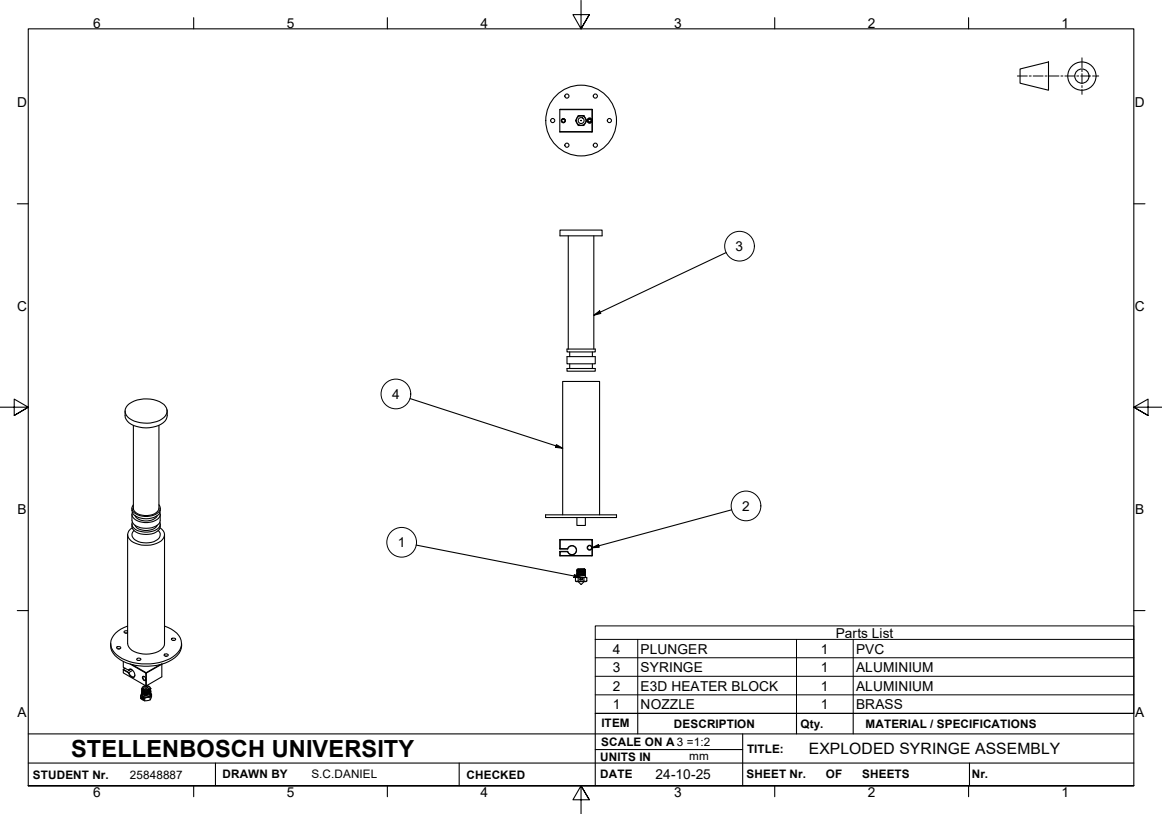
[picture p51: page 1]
Parts List; STUDENT Nr.; DRAWN BY; CHECKED; UNITS IN; SHEET Nr.; SHEETS

4 | PLUNGER | 1 | PVC
3 | SYRINGE | 1 | ALUMINIUM
2 | E3D HEATER BLOCK | 1 | ALUMINIUM
1 | NOZZLE | 1 | BRASS
ITEM | DESCRIPTION | Qty. | MATERIAL / SPECIFICATIONS

STELLENBOSCH UNIVERSITY | SCALE ON A 3 =1:2 | TITLE: EXPLODED SYRINGE ASSEMBLY

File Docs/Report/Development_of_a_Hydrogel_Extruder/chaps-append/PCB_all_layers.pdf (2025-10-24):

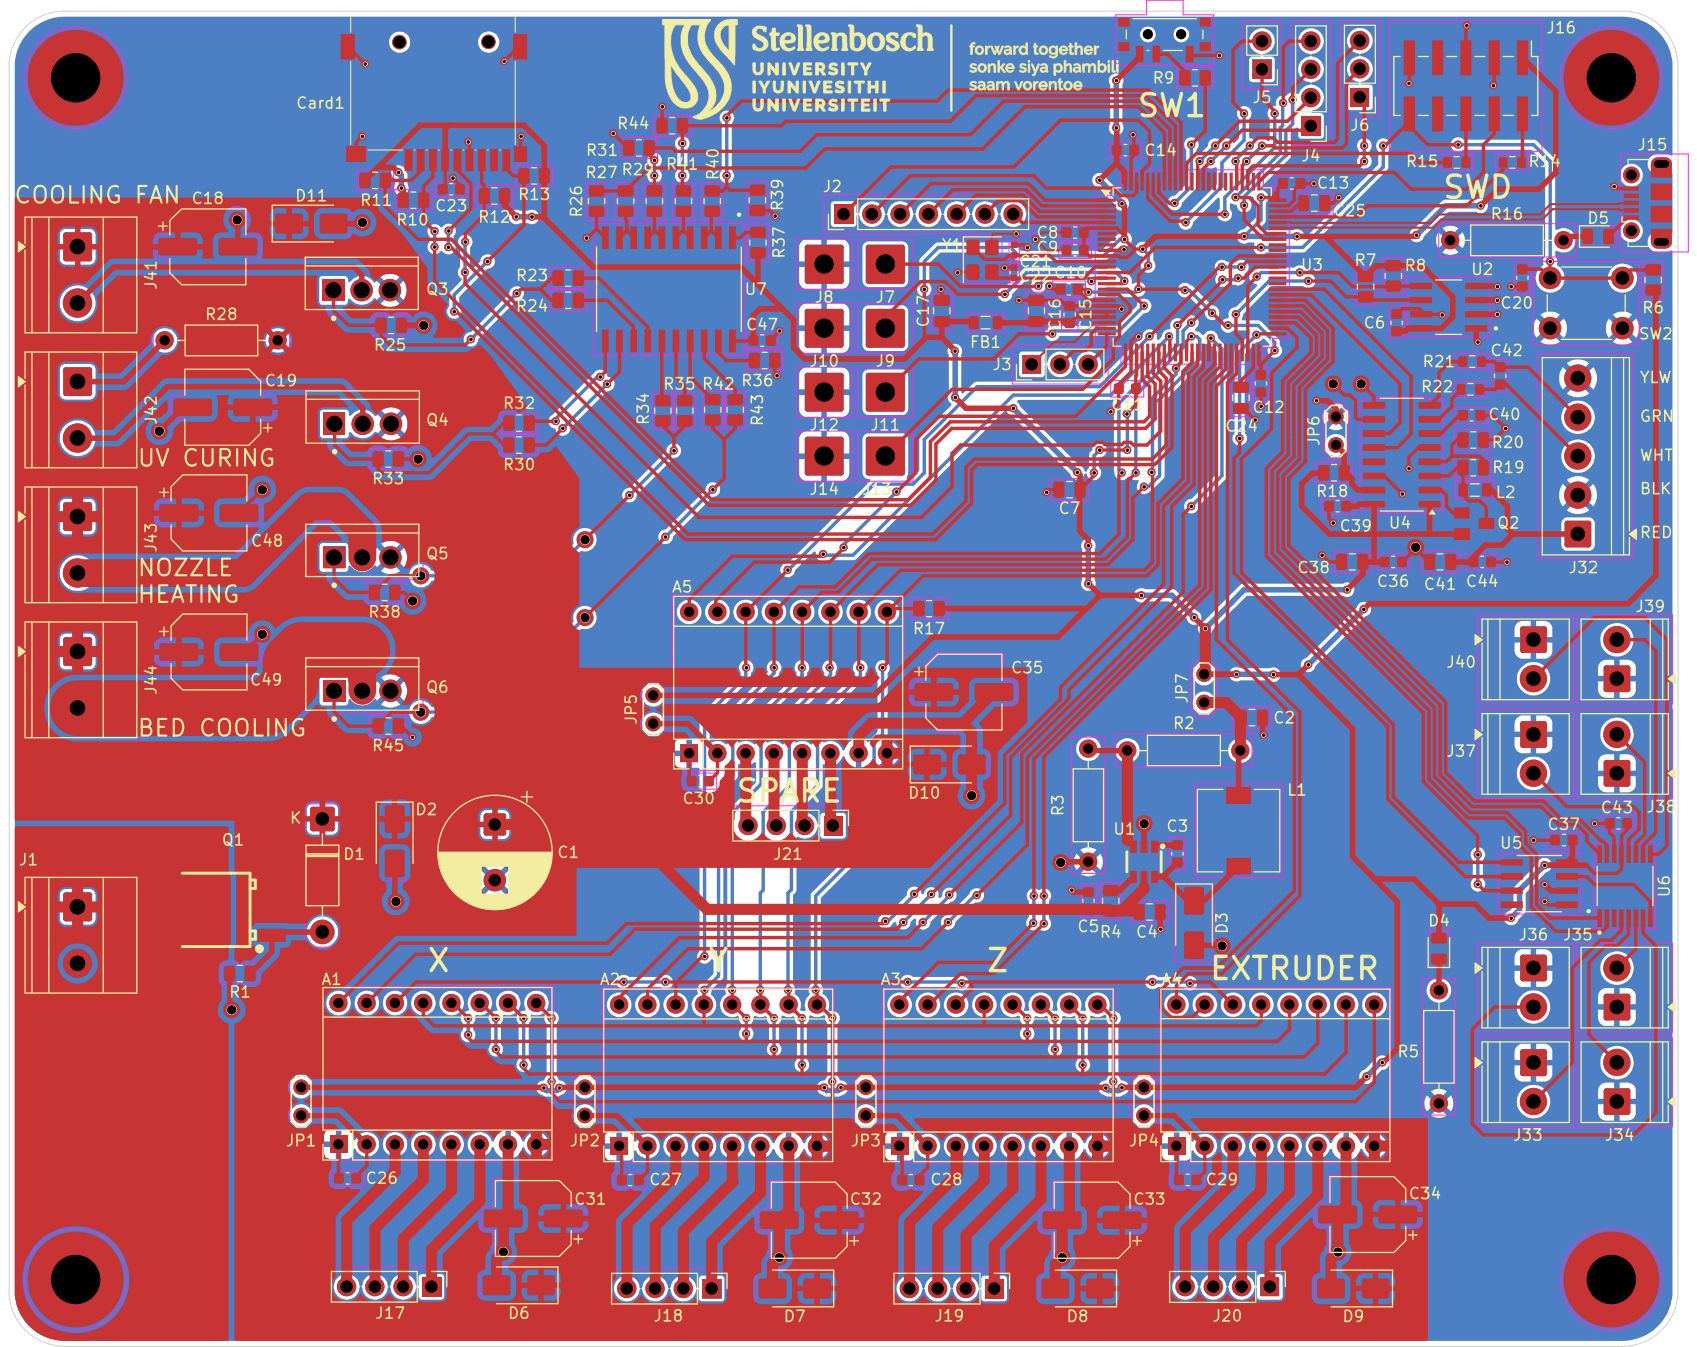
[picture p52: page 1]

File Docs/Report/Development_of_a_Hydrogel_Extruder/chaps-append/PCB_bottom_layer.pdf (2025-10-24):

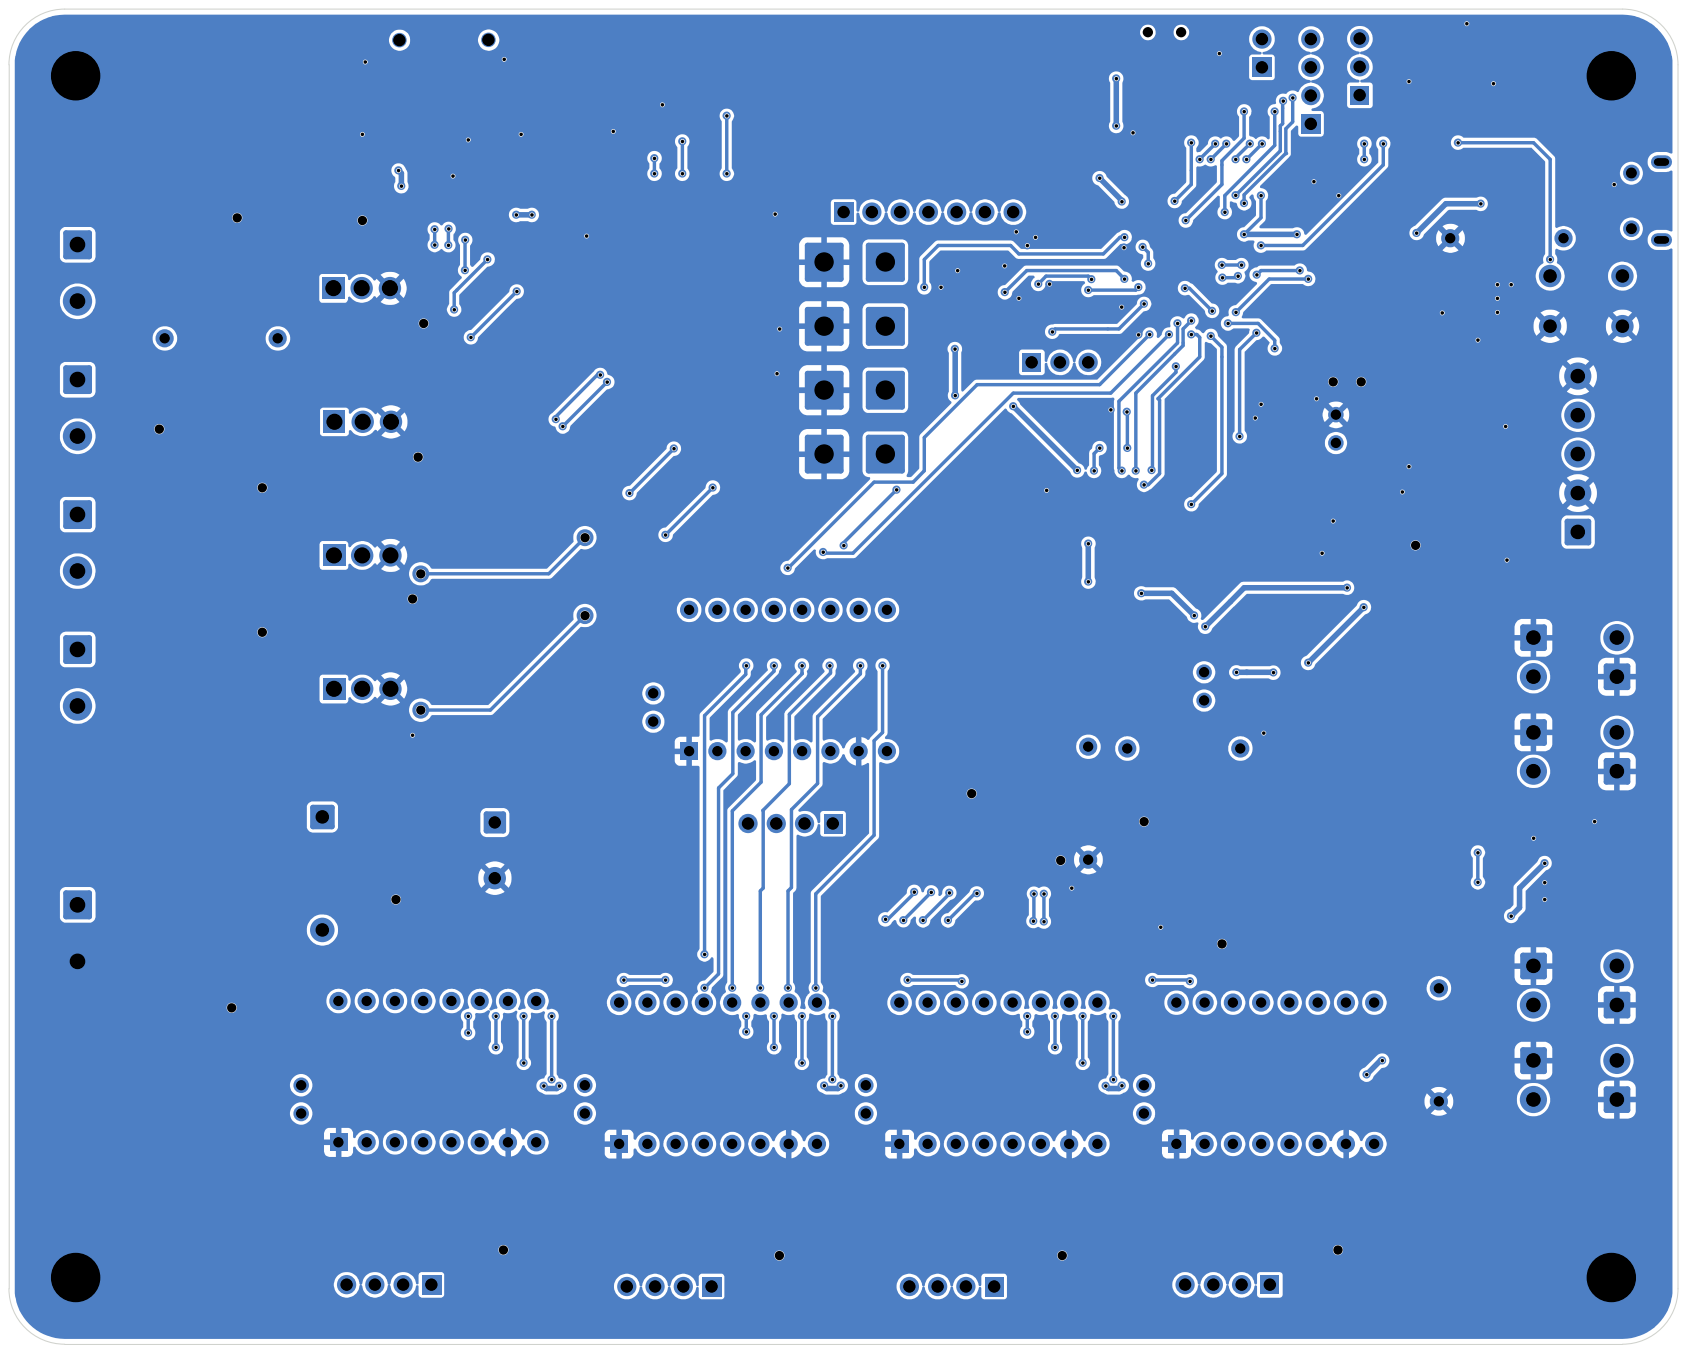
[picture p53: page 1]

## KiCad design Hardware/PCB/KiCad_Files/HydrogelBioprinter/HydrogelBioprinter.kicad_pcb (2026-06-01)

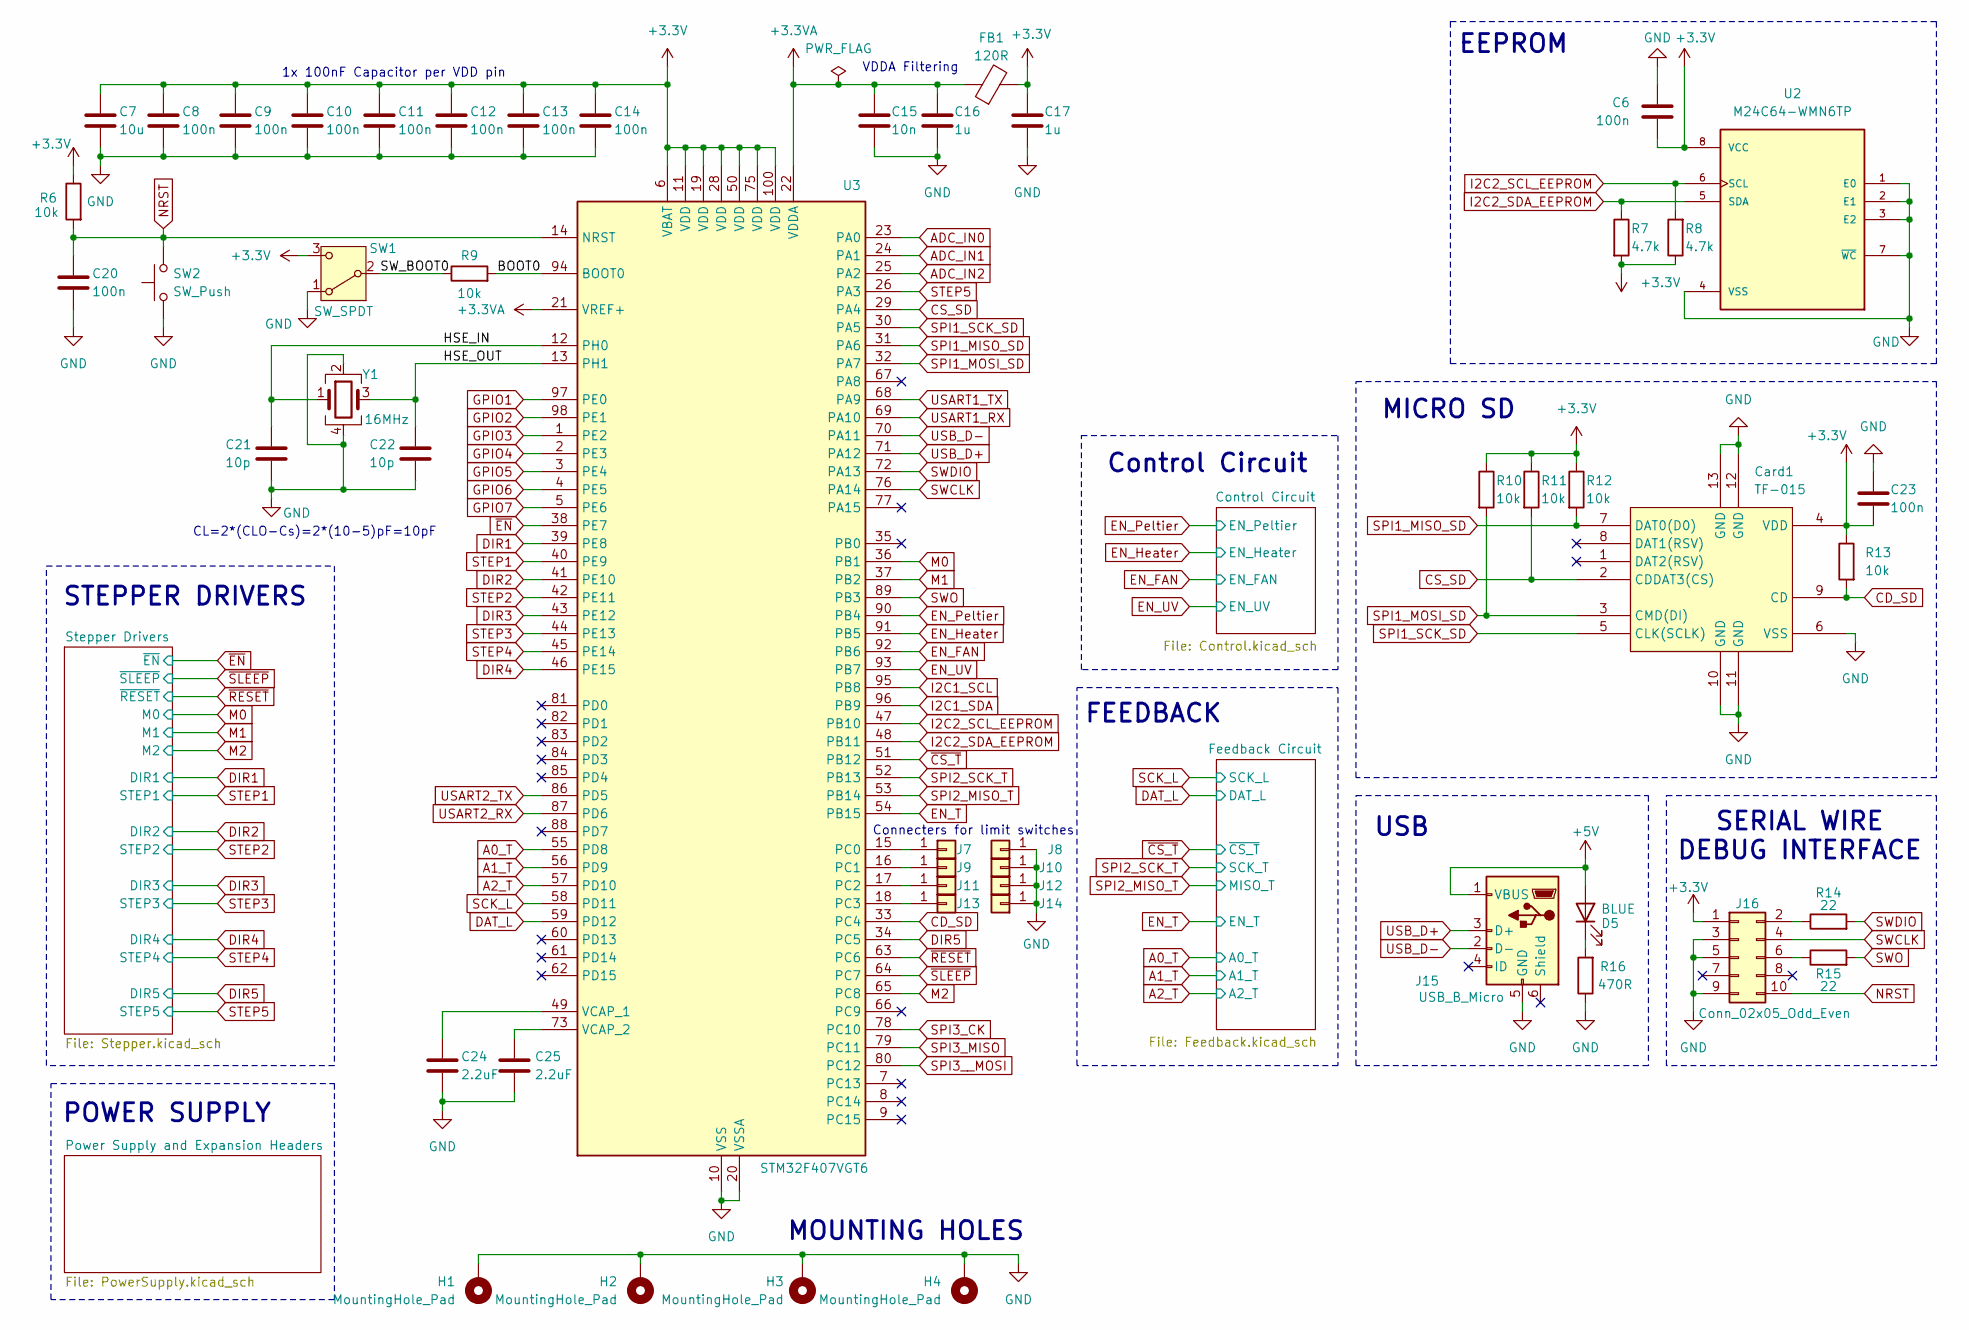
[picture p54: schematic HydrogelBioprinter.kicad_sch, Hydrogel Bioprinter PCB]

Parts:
C6, C8, C9, C10, C11, C12, C13, C14, C20, C23: 100n; C_0603_1608Metric
C7: 10u; C_0805_2012Metric
C15: 10n; C_0603_1608Metric
C16, C17: 1u; C_0805_2012Metric
C21, C22: 10p; C_0402_1005Metric
C24, C25: 2.2uF; C_0805_2012Metric
Card1: TF-015; TF-SMD_TF-015; LCSC Part C113206
D5: BLUE; LED_0805_2012Metric
FB1: 120R; L_0805_2012Metric
H1, H2, H3, H4: MountingHole_Pad; MountingHole_4.3mm_M4_Pad
J7, J8, J9, J10, J11, J12, J13, J14: Conn; SolderWire-0.75sqmm_1x01_D1.25mm_OD3.5mm
J15: USB_B_Micro; USB_Micro-B_Molex-105017-0001
J16: Conn_02x05_Odd_Even; PinHeader_2x05_P2.54mm_Vertical_SMD
R6, R9, R10, R11, R12, R13: 10k; R_0805_2012Metric
R7, R8: 4.7k; R_0805_2012Metric
R14, R15: 22; R_0603_1608Metric
R16: 470R; R_Axial_DIN0207_L6.3mm_D2.5mm_P10.16mm_Horizontal
SW1: SW_SPDT; SW_SPDT_PCM12
SW2: SW_Push; SW_PUSH_6mm
U2: M24C64-WMN6TP; SOIC127P600X175-8N; PARTREV 38; DigiKey_Part_Number 497-8650-2-ND
U3: STM32F407VGT6; LQFP-100_14x14mm_P0.5mm
Y1: 16MHz; Crystal_SMD_3225-4Pin_3.2x2.5mm

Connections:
+3.3V: C6.2, C7.1, C8.1, C9.1, C10.1, C11.1, C12.1, C13.1, C14.1, C17.1, C23.2, Card1.4 (VDD), FB1.2, J16.1, R6.1, R7.2, R8.1, R10.1, R11.1, R12.1, R13.1, SW1.3 (C), U2.8 (VCC), U3.6 (VBAT), U3.11 (VDD), U3.19 (VDD), U3.28 (VDD), U3.50 (VDD), U3.75 (VDD), U3.100 (VDD); also elsewhere on the board
+3.3VA: C15.1, C16.1, FB1.1, U3.21 (VREF+), U3.22 (VDDA)
+5V: D5.2 (A), J15.1 (VBUS)
/BOOT0: R9.2, U3.94 (BOOT0)
/HSE_IN: C21.1, U3.12 (PH0), Y1.1
/HSE_OUT: C22.1, U3.13 (PH1), Y1.3
/SW_BOOT0: R9.1, SW1.2 (B)
A0_T: U3.55 (PD8); also elsewhere on the board
A1_T: U3.56 (PD9); also elsewhere on the board
A2_T: U3.57 (PD10); also elsewhere on the board
ADC_IN0: U3.23 (PA0); also elsewhere on the board
ADC_IN1: U3.24 (PA1); also elsewhere on the board
ADC_IN2: U3.25 (PA2); also elsewhere on the board
CD_SD: Card1.9 (CD), R13.2, U3.33 (PC4)
CS_SD: Card1.2 (CDDAT3(CS)), R11.2, U3.29 (PA4)
DAT_L: U3.59 (PD12); also elsewhere on the board
DIR1: U3.39 (PE8); also elsewhere on the board
DIR2: U3.41 (PE10); also elsewhere on the board
DIR3: U3.43 (PE12); also elsewhere on the board
DIR4: U3.46 (PE15); also elsewhere on the board
DIR5: U3.34 (PC5); also elsewhere on the board
EN_FAN: U3.92 (PB6); also elsewhere on the board
EN_Heater: U3.91 (PB5); also elsewhere on the board
EN_Peltier: U3.90 (PB4); also elsewhere on the board
EN_T: U3.54 (PB15); also elsewhere on the board
EN_UV: U3.93 (PB7); also elsewhere on the board
GND: C6.1, C7.2, C8.2, C9.2, C10.2, C11.2, C12.2, C13.2, C14.2, C15.2, C16.2, C17.2, C20.2, C21.2, C22.2, C23.1, C24.2, C25.2, Card1.6 (VSS), Card1.10 (GND), Card1.11 (GND), Card1.12 (GND), Card1.13 (GND), H1.1, H2.1, H3.1, H4.1, J8.1, J10.1, J12.1, J14.1, J15.5 (GND), J16.3, J16.5, J16.9, R16.1, SW1.1 (A), SW2.1, U2.1 (E0), U2.2 (E1), U2.3 (E2), U2.4 (VSS), U2.7 (~WC), U3.10 (VSS), U3.20 (VSSA), U3.27 (VSS), U3.74 (VSS), U3.99 (VSS), Y1.2, Y1.4; also elsewhere on the board
GPIO1: U3.97 (PE0); also elsewhere on the board
GPIO2: U3.98 (PE1); also elsewhere on the board
GPIO3: U3.1 (PE2); also elsewhere on the board
GPIO4: U3.2 (PE3); also elsewhere on the board
GPIO5: U3.3 (PE4); also elsewhere on the board
GPIO6: U3.4 (PE5); also elsewhere on the board
GPIO7: U3.5 (PE6); also elsewhere on the board
I2C1_SCL: U3.95 (PB8); also elsewhere on the board
I2C1_SDA: U3.96 (PB9); also elsewhere on the board
I2C2_SCL_EEPROM: R8.2, U2.6 (SCL), U3.47 (PB10)
I2C2_SDA_EEPROM: R7.1, U2.5 (SDA), U3.48 (PB11)
M0: U3.36 (PB1); also elsewhere on the board
M1: U3.37 (PB2); also elsewhere on the board
M2: U3.65 (PC8); also elsewhere on the board
NRST: C20.1, J16.10, R6.2, SW2.2, U3.14 (NRST)
unnamed: D5.1 (K), R16.2
unnamed: J7.1, U3.15 (PC0)
unnamed: J9.1, U3.16 (PC1)
unnamed: J11.1, U3.17 (PC2)
unnamed: J13.1, U3.18 (PC3)
unnamed: J16.2, R14.1
unnamed: J16.6, R15.1
unnamed: C24.1, U3.49 (VCAP_1)
unnamed: C25.1, U3.73 (VCAP_2)
SCK_L: U3.58 (PD11); also elsewhere on the board
SPI1_MISO_SD: Card1.7 (DAT0(D0)), R12.2, U3.31 (PA6)
SPI1_MOSI_SD: Card1.3 (CMD(DI)), R10.2, U3.32 (PA7)
SPI1_SCK_SD: Card1.5 (CLK(SCLK)), U3.30 (PA5)
SPI2_MISO_T: U3.53 (PB14); also elsewhere on the board
SPI2_SCK_T: U3.52 (PB13); also elsewhere on the board
SPI3_CK: U3.78 (PC10); also elsewhere on the board
SPI3_MISO: U3.79 (PC11); also elsewhere on the board
SPI3__MOSI: U3.80 (PC12); also elsewhere on the board
STEP1: U3.40 (PE9); also elsewhere on the board
STEP2: U3.42 (PE11); also elsewhere on the board
STEP3: U3.44 (PE13); also elsewhere on the board
STEP4: U3.45 (PE14); also elsewhere on the board
STEP5: U3.26 (PA3); also elsewhere on the board
SWCLK: J16.4, U3.76 (PA14)
SWDIO: R14.2, U3.72 (PA13)
SWO: R15.2, U3.89 (PB3)
USART1_RX: U3.69 (PA10); also elsewhere on the board
USART1_TX: U3.68 (PA9); also elsewhere on the board
USART2_RX: U3.87 (PD6); also elsewhere on the board
USART2_TX: U3.86 (PD5); also elsewhere on the board
USB_D+: J15.3 (D+), U3.71 (PA12)
USB_D-: J15.2 (D-), U3.70 (PA11)
~CS_T: U3.51 (PB12); also elsewhere on the board
~EN: U3.38 (PE7); also elsewhere on the board
~RESET: U3.63 (PC6); also elsewhere on the board
~SLEEP: U3.64 (PC7); also elsewhere on the board

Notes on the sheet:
VDDA Filtering
FEEDBACK
SERIAL WIRE DEBUG INTERFACE
Connecters for limit switches
USB
MOUNTING HOLES
MICRO SD
STEPPER DRIVERS
CL=2*(CLO-Cs)=2*(10-5)pF=10pF
Control Circuit
EEPROM
POWER SUPPLY
1x 100nF Capacitor per VDD pin

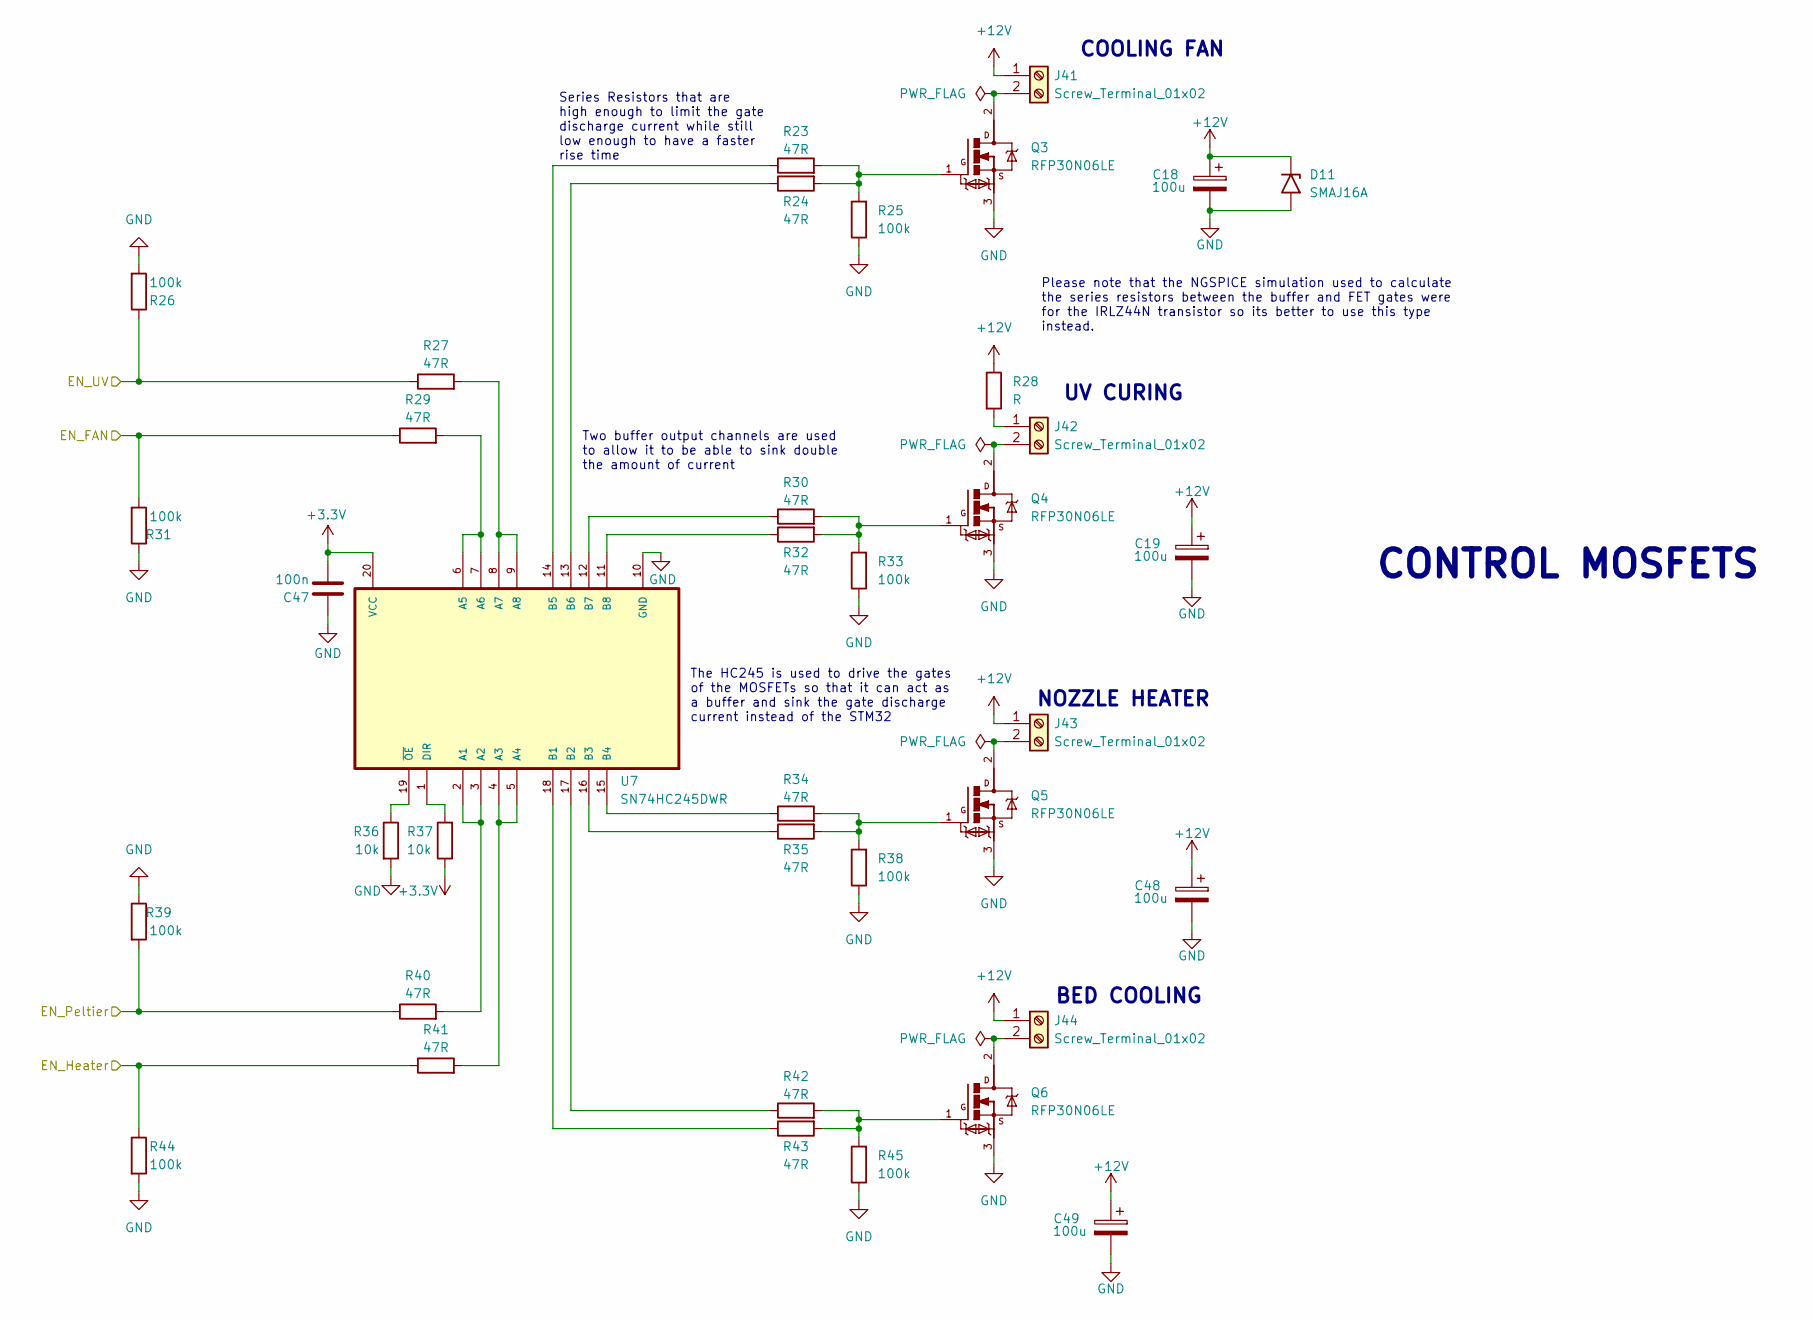
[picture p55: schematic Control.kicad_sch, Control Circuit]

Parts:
C18, C19, C48, C49: 100u; CP_Elec_6.3x7.7
C47: 100n; C_0603_1608Metric
D11: SMAJ16A; D_SMA
J41, J42, J43, J44: Screw_Terminal_01x02; TerminalBlock_Phoenix_MKDS-1,5-2-5.08_1x02_P5.08mm_Horizont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
Q3, Q4, Q5, Q6: RFP30N06LE; TRANS_RFP30N06LE
R23, R24, R27, R29, R30, R32, R34, R35, R40, R41, R42, R43: 47R; R_0805_2012Metric
R25, R26, R31, R33, R38, R39, R44, R45: 100k; R_0805_2012Metric
R28: R; R_Axial_DIN0207_L6.3mm_D2.5mm_P10.16mm_Horizontal
R36, R37: 10k; R_0805_2012Metric
U7: SN74HC245DWR; SOIC127P1030X265-20N

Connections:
+3.3V: C47.1, R37.1, U7.20 (VCC); also elsewhere on the board
+12V: C18.1, C19.1, C48.1, C49.1, D11.1 (A1), J41.1, J43.1, J44.1, R28.1; also elsewhere on the board
EN_FAN: R29.1, R31.2; also elsewhere on the board
EN_Heater: R41.1, R44.1; also elsewhere on the board
EN_Peltier: R39.2, R40.1; also elsewhere on the board
EN_UV: R26.1, R27.1; also elsewhere on the board
GND: C18.2, C19.2, C47.2, C48.2, C49.2, D11.2 (A2), Q3.3, Q4.3, Q5.3, Q6.3, R25.1, R26.2, R31.1, R33.1, R36.2, R38.1, R39.1, R44.2, R45.1, U7.10 (GND); also elsewhere on the board
unnamed: J41.2, Q3.2
unnamed: J42.1, R28.2
unnamed: J42.2, Q4.2
unnamed: J43.2, Q5.2
unnamed: J44.2, Q6.2
unnamed: Q3.1, R23.2, R24.2, R25.2
unnamed: Q4.1, R30.2, R32.2, R33.2
unnamed: Q5.1, R34.2, R35.2, R38.2
unnamed: Q6.1, R42.2, R43.2, R45.2
unnamed: R40.2, U7.2 (A1), U7.3 (A2)
unnamed: R41.2, U7.4 (A3), U7.5 (A4)
unnamed: R29.2, U7.6 (A5), U7.7 (A6)
unnamed: R27.2, U7.8 (A7), U7.9 (A8)
unnamed: R43.1, U7.18 (B1)
unnamed: R42.1, U7.17 (B2)
unnamed: R35.1, U7.16 (B3)
unnamed: R34.1, U7.15 (B4)
unnamed: R23.1, U7.14 (B5)
unnamed: R24.1, U7.13 (B6)
unnamed: R30.1, U7.12 (B7)
unnamed: R32.1, U7.11 (B8)
unnamed: R37.2, U7.1 (DIR)
unnamed: R36.1, U7.19 (~OE)

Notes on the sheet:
UV CURING
NOZZLE HEATER
COOLING FAN
Two buffer output channels are used to allow it to be able to sink double the amount of current
The HC245 is used to drive the gates of the MOSFETs so that it can act as a buffer and sink the gate discharge current instead of the STM32
Please note that the NGSPICE simulation used to calculate the series resistors between the buffer and FET gates were for the IRLZ44N transistor so its better to use this type instead.
CONTROL MOSFETS
Series Resistors that are high enough to limit the gate discharge current while still low enough to have a faster rise time
BED COOLING

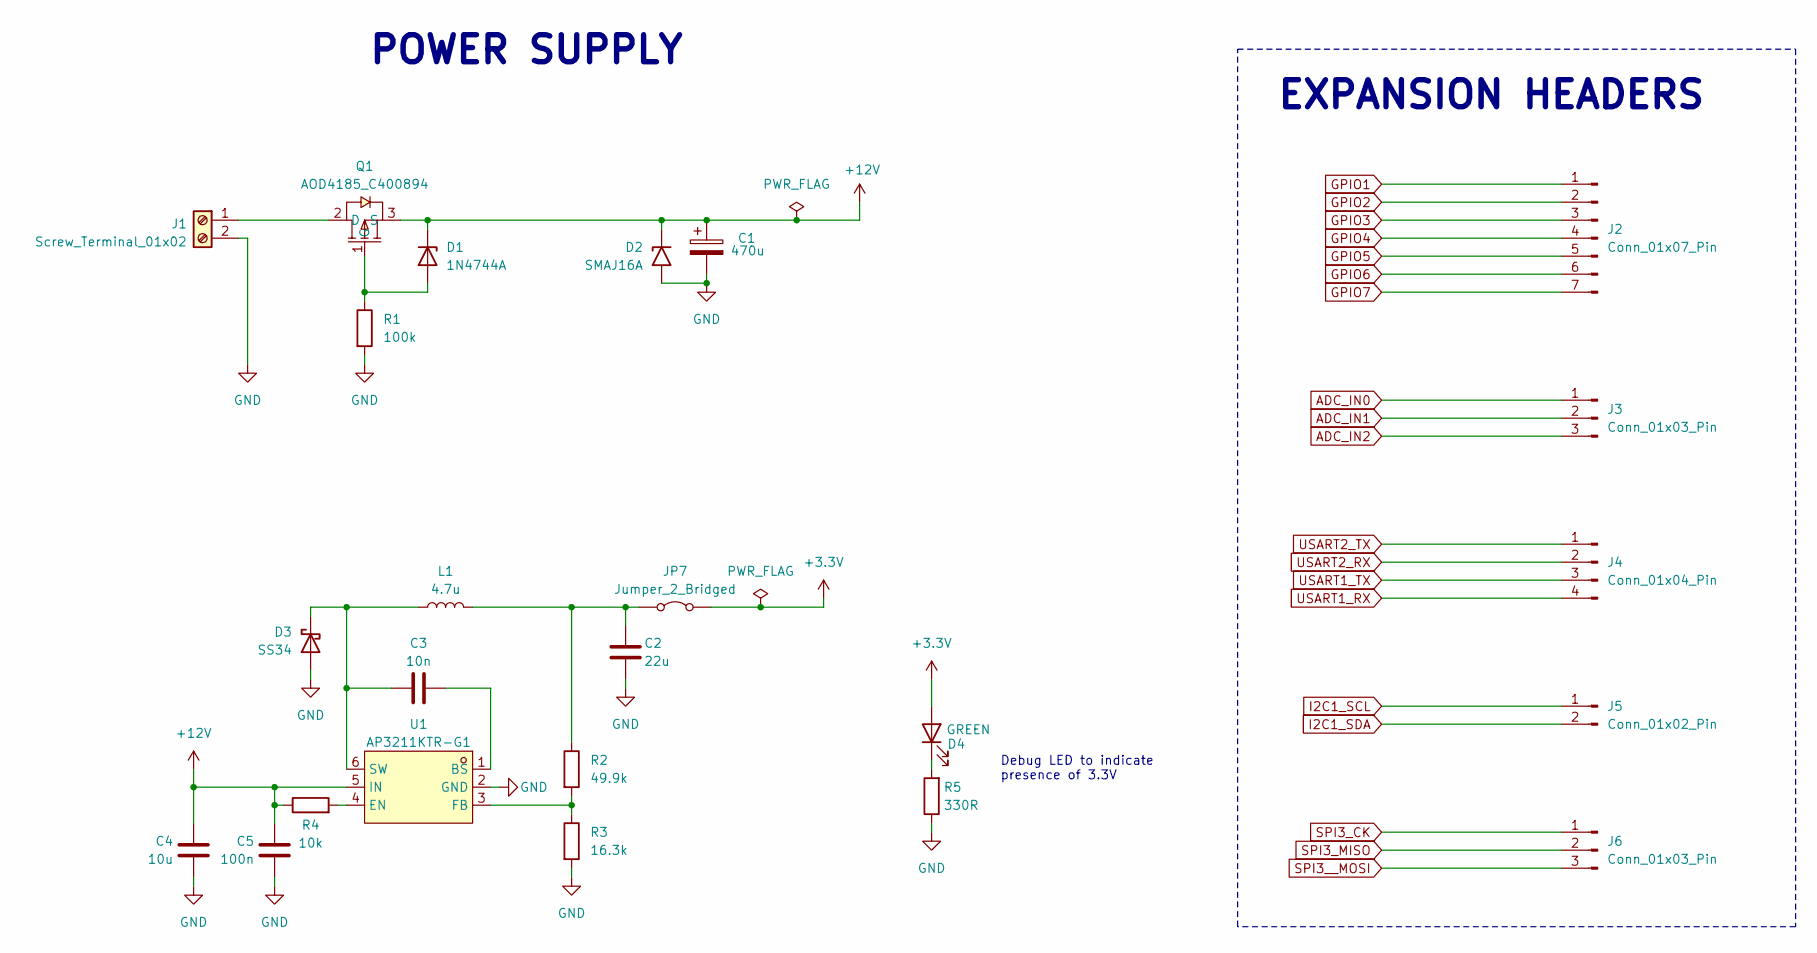
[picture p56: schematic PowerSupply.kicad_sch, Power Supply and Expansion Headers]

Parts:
C1: 470u; CP_Radial_D10.0mm_P5.00mm
C2: 22u; C_0805_2012Metric
C3: 10n; C_0603_1608Metric
C4: 10u; C_0805_2012Metric
C5: 100n; C_0603_1608Metric
D1: 1N4744A; D_DO-41_SOD81_P10.16mm_Horizontal
D2: SMAJ16A; D_SMA
D3: SS34; D_SMA
D4: GREEN; LED_0805_2012Metric
J1: Screw_Terminal_01x02; TerminalBlock_Phoenix_MKDS-1,5-2-5.08_1x02_P5.08mm_Horizont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
J2: Conn_01x07_Pin; PinHeader_1x07_P2.54mm_Vertical
J3, J6: Conn_01x03_Pin; PinHeader_1x03_P2.54mm_Vertical
J4: Conn_01x04_Pin; PinHeader_1x04_P2.54mm_Vertical
J5: Conn_01x02_Pin; PinHeader_1x02_P2.54mm_Vertical
JP7: Jumper_2_Bridged; TestPoint_2Pads_Pitch2.54mm_Drill0.8mm
L1: 4.7u; L_7.3x7.3_H4.5
Q1: AOD4185_C400894; TO-252-3_L6.6-W6.1-P4.57-LS9.9-BR-CW; LCSC Part C400894
R1: 100k; R_0805_2012Metric
R2: 49.9k; R_Axial_DIN0207_L6.3mm_D2.5mm_P10.16mm_Horizontal
R3: 16.3k; R_Axial_DIN0207_L6.3mm_D2.5mm_P10.16mm_Horizontal
R4: 10k; R_0805_2012Metric
R5: 330R; R_Axial_DIN0207_L6.3mm_D2.5mm_P10.16mm_Horizontal
U1: AP3211KTR-G1; LCSC Part C154863

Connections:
+3.3V: D4.2 (A), JP7.1 (A); also elsewhere on the board
+12V: C1.1, C4.2, C5.2, D1.1 (K), D2.1 (A1), Q1.3 (S), R4.1, U1.5 (IN); also elsewhere on the board
ADC_IN0: J3.1; also elsewhere on the board
ADC_IN1: J3.2; also elsewhere on the board
ADC_IN2: J3.3; also elsewhere on the board
GND: C1.2, C2.2, C4.1, C5.1, D2.2 (A2), D3.2 (A), J1.2, R1.2, R3.2, R5.1, U1.2 (GND); also elsewhere on the board
GPIO1: J2.1; also elsewhere on the board
GPIO2: J2.2; also elsewhere on the board
GPIO3: J2.3; also elsewhere on the board
GPIO4: J2.4; also elsewhere on the board
GPIO5: J2.5; also elsewhere on the board
GPIO6: J2.6; also elsewhere on the board
GPIO7: J2.7; also elsewhere on the board
I2C1_SCL: J5.1; also elsewhere on the board
I2C1_SDA: J5.2; also elsewhere on the board
unnamed: D1.2 (A), Q1.1 (G), R1.1
unnamed: C3.1, D3.1 (K), L1.1, U1.6 (SW)
unnamed: D4.1 (K), R5.2
unnamed: J1.1, Q1.2 (D)
unnamed: C2.1, JP7.2 (B), L1.2, R2.1
unnamed: C3.2, U1.1 (BS)
unnamed: R4.2, U1.4 (EN)
unnamed: R2.2, R3.1, U1.3 (FB)
SPI3_CK: J6.1; also elsewhere on the board
SPI3_MISO: J6.2; also elsewhere on the board
SPI3__MOSI: J6.3; also elsewhere on the board
USART1_RX: J4.4; also elsewhere on the board
USART1_TX: J4.3; also elsewhere on the board
USART2_RX: J4.2; also elsewhere on the board
USART2_TX: J4.1; also elsewhere on the board

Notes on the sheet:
EXPANSION HEADERS
POWER SUPPLY
Debug LED to indicate presence of 3.3V

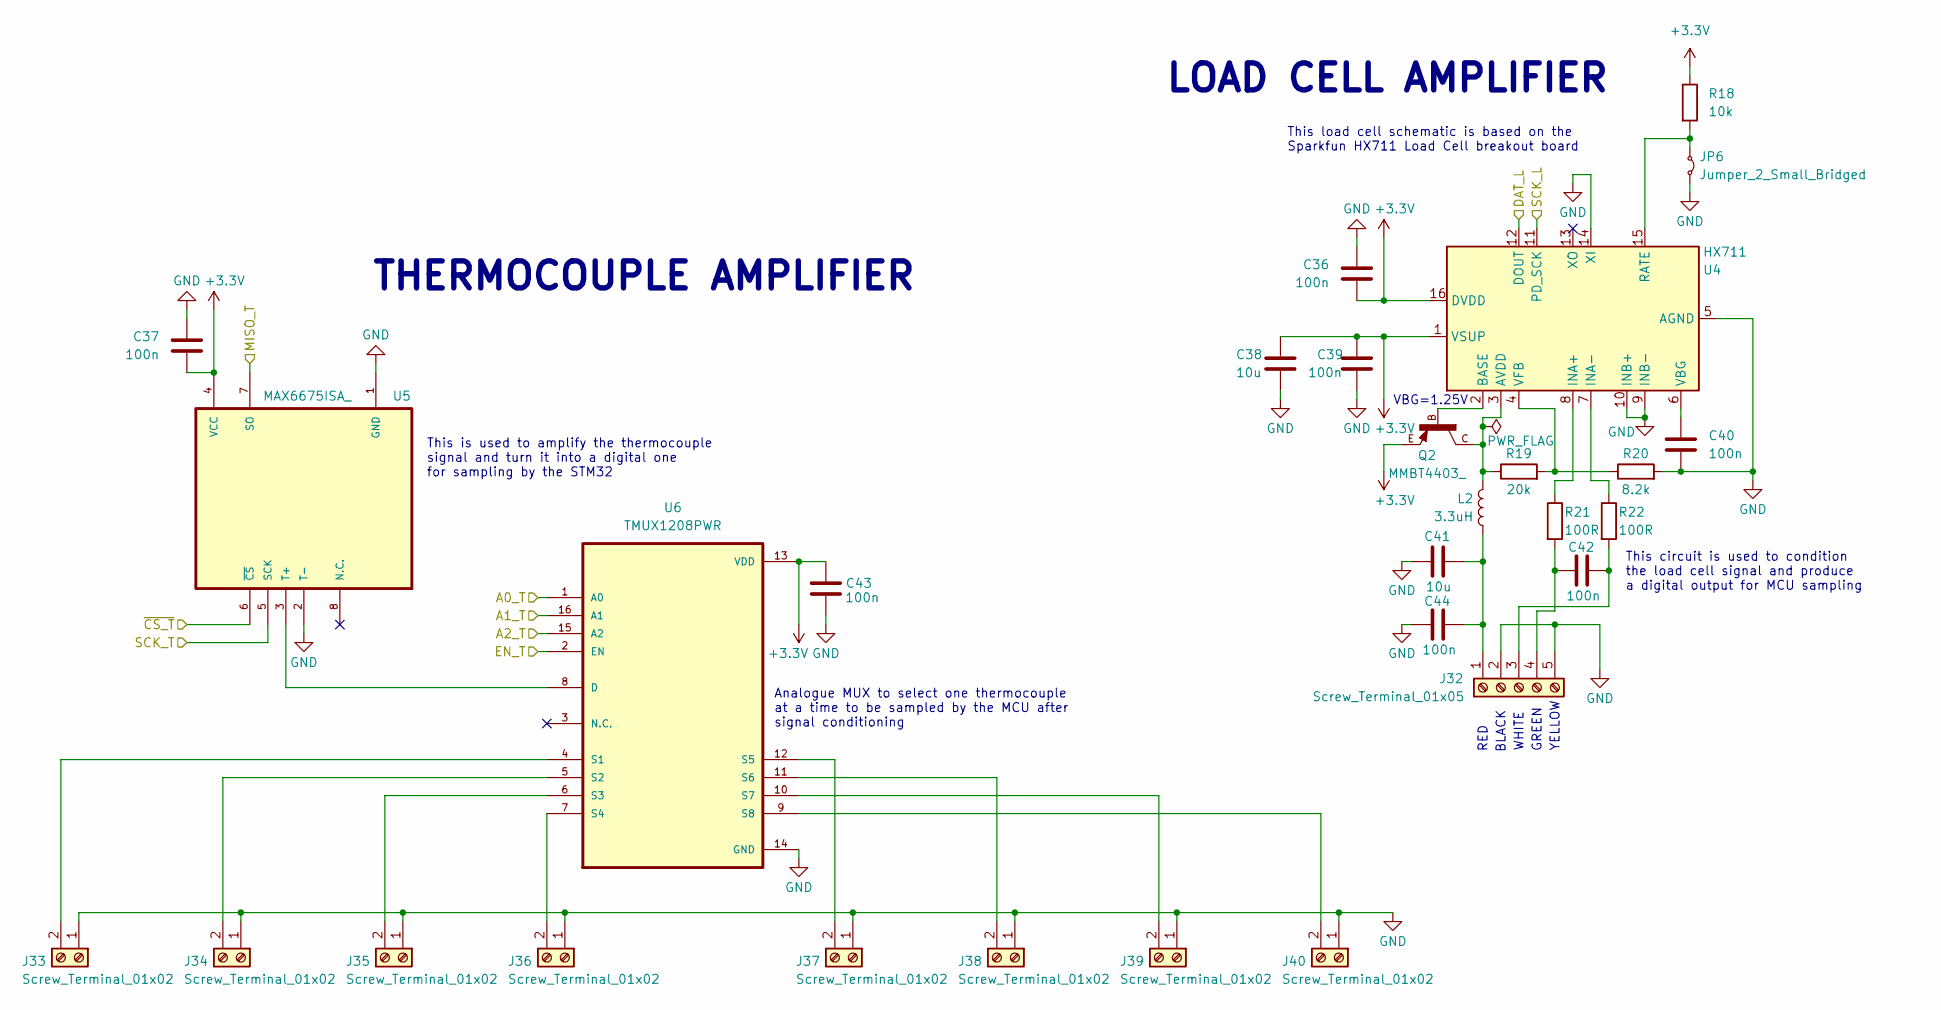
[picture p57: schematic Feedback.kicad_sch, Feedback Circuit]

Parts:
C36, C37, C39, C40, C42, C43, C44: 100n; C_0603_1608Metric
C38, C41: 10u; C_0805_2012Metric
J32: Screw_Terminal_01x05; TerminalBlock_Phoenix_PT-1,5-5-3.5-H_1x05_P3.50mm_Horizontal
J33, J34, J35, J36, J37, J38, J39, J40: Screw_Terminal_01x02; TerminalBlock_Phoenix_PT-1,5-2-3.5-H_1x02_P3.50mm_Horizontal
JP6: Jumper_2_Small_Bridged; TestPoint_2Pads_Pitch2.54mm_Drill0.8mm
L2: 3.3uH; L_0805_2012Metric
Q2: MMBT4403_; SOT23-BEC
R18: 10k; R_0805_2012Metric
R19: 20k; R_0805_2012Metric
R20: 8.2k; R_0805_2012Metric
R21, R22: 100R; R_0603_1608Metric
U4: HX711; SOP-16_3.9x9.9mm_P1.27mm
U5: MAX6675ISA_; SOIC127P600X175-8N
U6: TMUX1208PWR; SOP65P640X120-16N

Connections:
+3.3V: C36.2, C37.2, C38.2, C39.2, C43.2, Q2.E, R18.1, U4.1 (VSUP), U4.16 (DVDD), U5.4 (VCC), U6.13 (VDD); also elsewhere on the board
A0_T: U6.1 (A0); also elsewhere on the board
A1_T: U6.16 (A1); also elsewhere on the board
A2_T: U6.15 (A2); also elsewhere on the board
DAT_L: U4.12 (DOUT); also elsewhere on the board
EN_T: U6.2 (EN); also elsewhere on the board
GND: C36.1, C37.1, C38.1, C39.1, C40.2, C41.2, C43.1, C44.2, J32.2, J32.5, J33.1, J34.1, J35.1, J36.1, J37.1, J38.1, J39.1, J40.1, JP6.2 (B), R20.2, U4.5 (AGND), U4.9 (INB-), U4.10 (INB+), U4.14 (XI), U5.1 (GND), U5.2 (T-), U6.14 (GND); also elsewhere on the board
unnamed: C41.1, C44.1, J32.1, L2.2
unnamed: C42.1, J32.3, R22.2
unnamed: C42.2, J32.4, R21.2
unnamed: J33.2, U6.4 (S1)
unnamed: J34.2, U6.5 (S2)
unnamed: J35.2, U6.6 (S3)
unnamed: J36.2, U6.7 (S4)
unnamed: J37.2, U6.12 (S5)
unnamed: J38.2, U6.11 (S6)
unnamed: J39.2, U6.10 (S7)
unnamed: J40.2, U6.9 (S8)
unnamed: JP6.1 (A), R18.2, U4.15 (RATE)
unnamed: L2.1, Q2.C, R19.1, U4.3 (AVDD)
unnamed: Q2.B, U4.2 (BASE)
unnamed: R21.1, U4.8 (INA+)
unnamed: R22.1, U4.7 (INA-)
unnamed: C40.1, U4.6 (VBG)
unnamed: R19.2, R20.1, U4.4 (VFB)
unnamed: U5.3 (T+), U6.8 (D)
SCK_L: U4.11 (PD_SCK); also elsewhere on the board
SPI2_MISO_T: U5.7 (SO); also elsewhere on the board
SPI2_SCK_T: U5.5 (SCK); also elsewhere on the board
~CS_T: U5.6 (~CS); also elsewhere on the board

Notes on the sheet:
WHITE
This load cell schematic is based on the Sparkfun HX711 Load Cell breakout board
THERMOCOUPLE AMPLIFIER
YELLOW
This circuit is used to condition the load cell signal and produce a digital output for MCU sampling
BLACK
RED
GREEN
Analogue MUX to select one thermocouple at a time to be sampled by the MCU after signal conditioning
LOAD CELL AMPLIFIER
VBG=1.25V
This is used to amplify the thermocouple signal and turn it into a digital one for sampling by the STM32

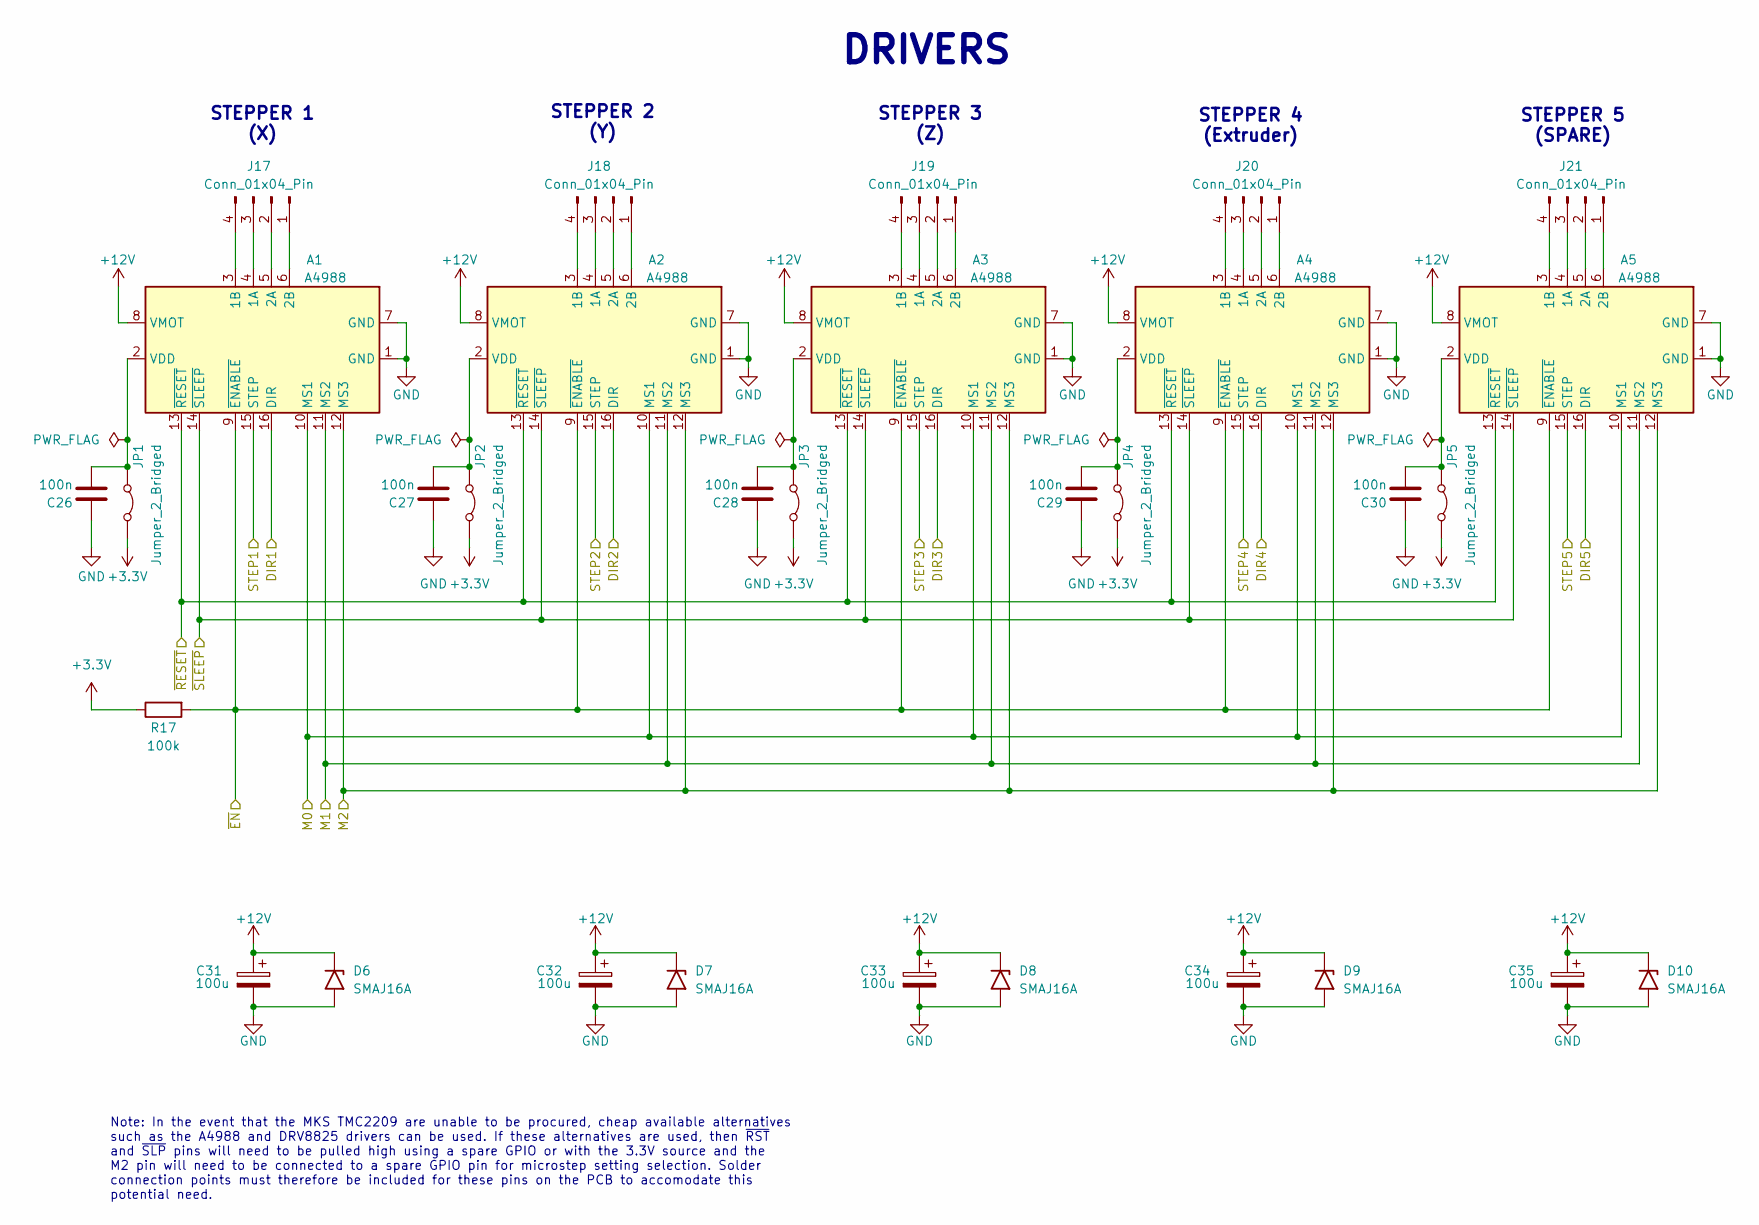
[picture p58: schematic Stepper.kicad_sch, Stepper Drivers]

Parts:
A1, A2, A3, A4, A5: A4988; Pololu_Breakout-16_15.2x20.3mm
C26, C27, C28, C29, C30: 100n; C_0603_1608Metric
C31, C32, C33, C34, C35: 100u; CP_Elec_6.3x7.7
D6, D7, D8, D9, D10: SMAJ16A; D_SMA
J17, J18, J19, J20, J21: Conn_01x04_Pin; PinHeader_1x04_P2.54mm_Vertical
JP1, JP2, JP3, JP4, JP5: Jumper_2_Bridged; TestPoint_2Pads_Pitch2.54mm_Drill0.8mm
R17: 100k; R_0805_2012Metric

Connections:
+3.3V: JP1.2 (B), JP2.2 (B), JP3.2 (B), JP4.2 (B), JP5.2 (B), R17.1; also elsewhere on the board
+12V: A1.8 (VMOT), A2.8 (VMOT), A3.8 (VMOT), A4.8 (VMOT), A5.8 (VMOT), C31.1, C32.1, C33.1, C34.1, C35.1, D6.1 (A1), D7.1 (A1), D8.1 (A1), D9.1 (A1), D10.1 (A1); also elsewhere on the board
DIR1: A1.16 (DIR); also elsewhere on the board
DIR2: A2.16 (DIR); also elsewhere on the board
DIR3: A3.16 (DIR); also elsewhere on the board
DIR4: A4.16 (DIR); also elsewhere on the board
DIR5: A5.16 (DIR); also elsewhere on the board
GND: A1.1 (GND), A1.7 (GND), A2.1 (GND), A2.7 (GND), A3.1 (GND), A3.7 (GND), A4.1 (GND), A4.7 (GND), A5.1 (GND), A5.7 (GND), C26.1, C27.1, C28.1, C29.1, C30.1, C31.2, C32.2, C33.2, C34.2, C35.2, D6.2 (A2), D7.2 (A2), D8.2 (A2), D9.2 (A2), D10.2 (A2); also elsewhere on the board
M0: A1.10 (MS1), A2.10 (MS1), A3.10 (MS1), A4.10 (MS1), A5.10 (MS1); also elsewhere on the board
M1: A1.11 (MS2), A2.11 (MS2), A3.11 (MS2), A4.11 (MS2), A5.11 (MS2); also elsewhere on the board
M2: A1.12 (MS3), A2.12 (MS3), A3.12 (MS3), A4.12 (MS3), A5.12 (MS3); also elsewhere on the board
unnamed: A1.4 (1A), J17.3
unnamed: A1.3 (1B), J17.4
unnamed: A1.5 (2A), J17.2
unnamed: A1.6 (2B), J17.1
unnamed: A1.2 (VDD), C26.2, JP1.1 (A)
unnamed: A2.4 (1A), J18.3
unnamed: A2.3 (1B), J18.4
unnamed: A2.5 (2A), J18.2
unnamed: A2.6 (2B), J18.1
unnamed: A2.2 (VDD), C27.2, JP2.1 (A)
unnamed: A3.4 (1A), J19.3
unnamed: A3.3 (1B), J19.4
unnamed: A3.5 (2A), J19.2
unnamed: A3.6 (2B), J19.1
unnamed: A3.2 (VDD), C28.2, JP3.1 (A)
unnamed: A4.4 (1A), J20.3
unnamed: A4.3 (1B), J20.4
unnamed: A4.5 (2A), J20.2
unnamed: A4.6 (2B), J20.1
unnamed: A4.2 (VDD), C29.2, JP4.1 (A)
unnamed: A5.4 (1A), J21.3
unnamed: A5.3 (1B), J21.4
unnamed: A5.5 (2A), J21.2
unnamed: A5.6 (2B), J21.1
unnamed: A5.2 (VDD), C30.2, JP5.1 (A)
STEP1: A1.15 (STEP); also elsewhere on the board
STEP2: A2.15 (STEP); also elsewhere on the board
STEP3: A3.15 (STEP); also elsewhere on the board
STEP4: A4.15 (STEP); also elsewhere on the board
STEP5: A5.15 (STEP); also elsewhere on the board
~EN: A1.9 (~ENABLE), A2.9 (~ENABLE), A3.9 (~ENABLE), A4.9 (~ENABLE), A5.9 (~ENABLE), R17.2; also elsewhere on the board
~RESET: A1.13 (~RESET), A2.13 (~RESET), A3.13 (~RESET), A4.13 (~RESET), A5.13 (~RESET); also elsewhere on the board
~SLEEP: A1.14 (~SLEEP), A2.14 (~SLEEP), A3.14 (~SLEEP), A4.14 (~SLEEP), A5.14 (~SLEEP); also elsewhere on the board

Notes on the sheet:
STEPPER 1 (X)
STEPPER 3 (Z)
STEPPER 2 (Y)
DRIVERS
STEPPER 5 (SPARE)
STEPPER 4 (Extruder)
Note: In the event that the MKS TMC2209 are unable to be procured, cheap available alternatives such as the A4988 and DRV8825 drivers can be used. If these alternatives are used, then ~{RST} and ~{SLP} pins will need to be pulled high using a spare GPIO or with the 3.3V source and the M2 pin will n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

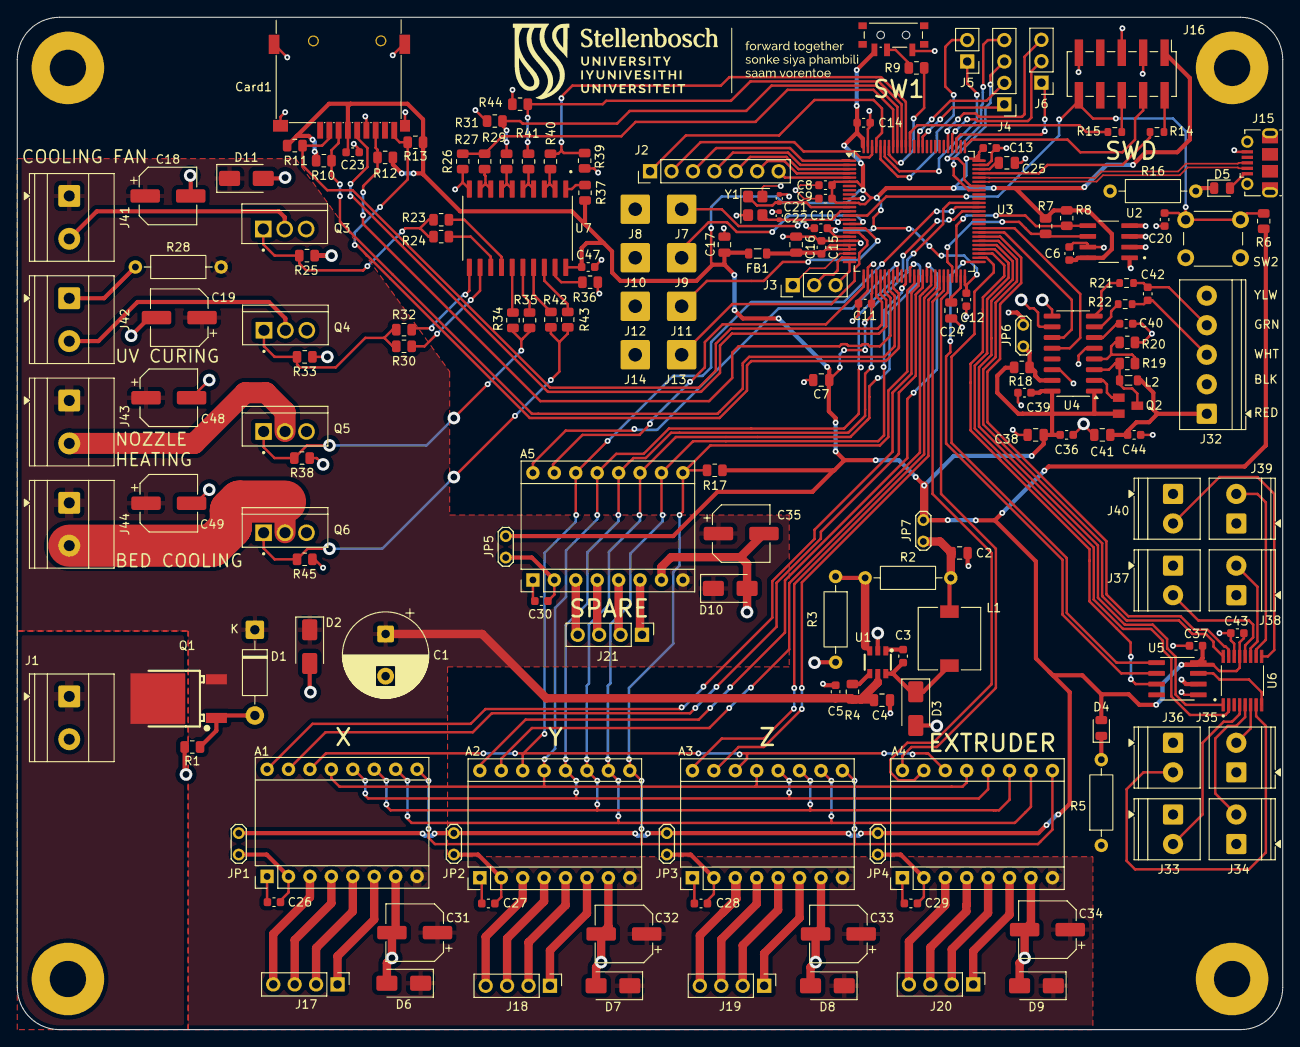
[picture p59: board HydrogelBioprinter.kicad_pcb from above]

Board: 2 copper layers, 150.0 x 120.0 mm, 173 parts (0 on the bottom side), 154 nets.

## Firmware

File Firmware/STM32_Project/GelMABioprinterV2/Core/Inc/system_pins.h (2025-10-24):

/*
 * system_pins.h
 *
 *  Created on: Sep 10, 2025
 *      Author: Simon
 */

#ifndef INC_SYSTEM_PINS_H_
#define INC_SYSTEM_PINS_H_

#pragma once
#include "main.h"

/* ----------------------------- STEPPER PINS ------------------------------- */
// Universal A4988 Pins
#define EN_Port    	  GPIOE
#define EN_Pin		  GPIO_PIN_7
#define SLEEP_Port    GPIOC
#define SLEEP_Pin     GPIO_PIN_7
#define RESET_Port    GPIOC
#define RESET_Pin     GPIO_PIN_6
#define M0_Port       GPIOB
#define M0_Pin        GPIO_PIN_1
#define M1_Port       GPIOB
#define M1_Pin        GPIO_PIN_2
#define M2_Port    	  GPIOC
#define M2_Pin        GPIO_PIN_8

// X axis
#define STEP_X_Port   GPIOE
#define STEP_X_Pin    GPIO_PIN_9
#define DIR_X_Port    GPIOE
#define DIR_X_Pin     GPIO_PIN_8

// Y axis
#define STEP_Y_Port   GPIOE
#define STEP_Y_Pin    GPIO_PIN_11
#define DIR_Y_Port    GPIOE
#define DIR_Y_Pin     GPIO_PIN_10

// Z axis
#define STEP_Z_Port   GPIOE
#define STEP_Z_Pin    GPIO_PIN_13
#define DIR_Z_Port    GPIOE
#define DIR_Z_Pin     GPIO_PIN_12

// E (extruder)
#define STEP_E_Port   GPIOE
#define STEP_E_Pin    GPIO_PIN_14
#define DIR_E_Port    GPIOE
#define DIR_E_Pin     GPIO_PIN_15

/* --------------------------- LIMIT SWITCH PINS ---------------------------- */
// X axis
#define LIMIT_X_Port   GPIOC
#define LIMIT_X_Pin    GPIO_PIN_0

// Y axis
#define LIMIT_Y_Port   GPIOC
#define LIMIT_Y_Pin    GPIO_PIN_1

// Z axis
#define LIMIT_Z_Port   GPIOC
#define LIMIT_Z_Pin    GPIO_PIN_2


/* ------------------------------- MUX PINS --------------------------------- */
// TMUX1208 select pins (A0, A1, & A2) and EN.
#define MUX_A0_Port   GPIOD
#define MUX_A0_Pin    GPIO_PIN_8
#define MUX_A1_Port   GPIOD
#define MUX_A1_Pin    GPIO_PIN_9
#define MUX_A2_Port   GPIOD
#define MUX_A2_Pin    GPIO_PIN_10
#define MUX_EN_Port   GPIOB
#define MUX_EN_Pin    GPIO_PIN_15

// EN active high; inactive low
#define MUX_ENABLE    GPIO_PIN_SET
#define MUX_DISABLE   GPIO_PIN_RESET


/* --------------------------- SWITCHING MOSFETS ---------------------------- */
// Peltier
#define PELTIER_GPIO_Port	GPIOB
#define PELTIER_GPIO_Pin    GPIO_PIN_4

// Nozzle heater (PB5)
#define NOZZLE_TIM          (&htim3)
#define NOZZLE_TIM_CH       TIM_CHANNEL_2

// Cooling Fan (PB6)
#define FAN_TIM             (&htim4)
#define FAN_TIM_CH          TIM_CHANNEL_1

// UV Curing (PB7)
#define UV_TIM              (&htim4)
#define UV_TIM_CH           TIM_CHANNEL_2

// External TIM handles provided by CubeMX code
extern TIM_HandleTypeDef htim3;
extern TIM_HandleTypeDef htim4;


#endif /* INC_SYSTEM_PINS_H_ */

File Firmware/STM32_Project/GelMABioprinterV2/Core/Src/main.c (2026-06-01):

/* USER CODE BEGIN Header */
/**
  ******************************************************************************
  * @file           : main.c
  * @brief          : Main program body
  ******************************************************************************
  * @attention
  *
  * Copyright (c) 2025 STMicroelectronics.
  * All rights reserved.
  *
  * This software is licensed under terms that can be found in the LICENSE file
  * in the root directory of this software component.
  * If no LICENSE file comes with this software, it is provided AS-IS.
  *
  ******************************************************************************
  */
/* USER CODE END Header */
/* Includes ------------------------------------------------------------------*/
#include "main.h"
#include "fatfs.h"
#include "usb_device.h"

/* Private includes ----------------------------------------------------------*/
/* USER CODE BEGIN Includes */
#include <math.h>
#include "string.h"
#include <stdarg.h>
#include <stdio.h>
#include "usbd_def.h"
#include "usbd_cdc_if.h"
#include "system_pins.h"
#include "delay_us.h"
#include "stepper.h"
#include "mosfet.h"
/* USER CODE END Includes */

/* Private typedef -----------------------------------------------------------*/
/* USER CODE BEGIN PTD */

/* USER CODE END PTD */

/* Private define ------------------------------------------------------------*/
/* USER CODE BEGIN PD */

/* USER CODE END PD */

/* Private macro -------------------------------------------------------------*/
/* USER CODE BEGIN PM */

/* USER CODE END PM */

/* Private variables ---------------------------------------------------------*/
I2C_HandleTypeDef hi2c2;

SPI_HandleTypeDef hspi1;
SPI_HandleTypeDef hspi3;

TIM_HandleTypeDef htim1;
TIM_HandleTypeDef htim2;
TIM_HandleTypeDef htim3;
TIM_HandleTypeDef htim4;
TIM_HandleTypeDef htim5;

/* USER CODE BEGIN PV */

static float setNozTempCmd = 40.0f; // Nozzle set temperature
static float nozDutyCmd = 0.0f;

/* PID variables */
static float pid_Kp = 3.0f;
static float pid_Ki = 0.1f;
static float pid_Kd = 3.0f;

static float pid_integral = 0.0f;
static float pid_prevError = 0.0f;
static uint8_t pid_firstRun = 1;

static uint8_t oneTimeDone = 0;
static float tempsC[8] = {0};
//static uint8_t muxIndex = 0;
//static uint32_t lastTempKickMs = 0;
static uint32_t lastUsbTxMs = 0;
static uint32_t lastPwmUpdateMs = 0;

// SD card variables
static FATFS   s_fs;                   // filesystem object
static FIL     s_file;                 // open CSV
static uint8_t s_sdReady = 0;          // 0=not mounted/opened yet
static uint8_t s_headerSkipped = 0;
static uint32_t s_lastSDms = 0;        // throttle
static char    s_line[160];            // one CSV line buffer
static uint8_t s_havePendingLine = 0;
static char s_pendingLine[160];
uint8_t rx_buf[2];
uint8_t tx_buf[2] = {0x00, 0x00};   // dummy bytes to generate clock
char msg[100];
/* USER CODE END PV */

/* Private function prototypes -----------------------------------------------*/
void SystemClock_Config(void);
static void MX_GPIO_Init(void);
static void MX_TIM1_Init(void);
static void MX_TIM2_Init(void);
static void MX_SPI1_Init(void);
static void MX_TIM3_Init(void);
static void MX_TIM4_Init(void);
static void MX_I2C2_Init(void);
static void MX_TIM5_Init(void);
static void MX_SPI3_Init(void);
/* USER CODE BEGIN PFP */
void Home(TIM_HandleTypeDef *htim_for_delay);
static void Task_Once_StorageInit(void);
static void USB_Printf(const char *fmt, ...);
static void Task_PIDandStreamUSB(void);
static void Task_ReadSD(void);
static void Task_UpdatePWMs(void);
uint16_t MAX6675_ReadRaw(void);
float MAX6675_ReadTemp(void);
void SystemTasks(void);
/* USER CODE END PFP */

/* Private user code ---------------------------------------------------------*/
/* USER CODE BEGIN 0 */

/* USER CODE END 0 */

/**
  * @brief  The application entry point.
  * @retval int
  */
int main(void)
{

  /* USER CODE BEGIN 1 */

  /* USER CODE END 1 */

  /* MCU Configuration--------------------------------------------------------*/

  /* Reset of all peripherals, Initializes the Flash interface and the Systick. */
  HAL_Init();

  /* USER CODE BEGIN Init */

  /* USER CODE END Init */

  /* Configure the system clock */
  SystemClock_Config();

  /* USER CODE BEGIN SysInit */

  /* USER CODE END SysInit */

  /* Initialize all configured peripherals */
  MX_GPIO_Init();
  MX_TIM1_Init();
  MX_USB_DEVICE_Init();
  MX_TIM2_Init();
  MX_SPI1_Init();
  MX_FATFS_Init();
  MX_TIM3_Init();
  MX_TIM4_Init();
  MX_I2C2_Init();
  MX_TIM5_Init();
  MX_SPI3_Init();
  /* USER CODE BEGIN 2 */
  HAL_GPIO_WritePin(PELTIER_GPIO_Port, PELTIER_GPIO_Pin, GPIO_PIN_SET); // Give the bed time to cool


  extern TIM_HandleTypeDef htim5;
  Home(&htim5);

  // Start the stepper ISR scheduler on TIM1
  Stepper_Init_TIM1();
  Stepper_ResetPosition(0,0,0,0);
  //Stepper_QueueAbs(135, 190.5, -98.5, 0, 30 );// The iteratively solved bed center
  //Stepper_QueueAbs(210, 270, -90, 0, 40 );
  //Stepper_QueueAbs(210, 270, -90, 10, 2 );
  //Stepper_QueueAbs(210,0,0,31,40);

  Mosfet_Init();
  HAL_GPIO_WritePin(PELTIER_GPIO_Port, PELTIER_GPIO_Pin, GPIO_PIN_SET); // Give the bed time to cool
  HAL_TIM_Base_Start(&htim2);
  /* USER CODE END 2 */

  /* Infinite loop */
  /* USER CODE BEGIN WHILE */
  //HAL_GPIO_WritePin(SSPORT, SSPIN, GPIO_PIN_SET);
  while (1)
  {
	SystemTasks();
    /* USER CODE END WHILE */

    /* USER CODE BEGIN 3 */
  }
  /* USER CODE END 3 */
}

/**
  * @brief System Clock Configuration
  * @retval None
  */
void SystemClock_Config(void)
{
  RCC_OscInitTypeDef RCC_OscInitStruct = {0};
  RCC_ClkInitTypeDef RCC_ClkInitStruct = {0};

  /** Configure the main internal regulator output voltage
  */
  __HAL_RCC_PWR_CLK_ENABLE();
  __HAL_PWR_VOLTAGESCALING_CONFIG(PWR_REGULATOR_VOLTAGE_SCALE1);

  /** Initializes the RCC Oscillators according to the specified parameters
  * in the RCC_OscInitTypeDef structure.
  */
  RCC_OscInitStruct.OscillatorType = RCC_OSCILLATORTYPE_HSE;
  RCC_OscInitStruct.HSEState = RCC_HSE_ON;
  RCC_OscInitStruct.PLL.PLLState = RCC_PLL_ON;
  RCC_OscInitStruct.PLL.PLLSource = RCC_PLLSOURCE_HSE;
  RCC_OscInitStruct.PLL.PLLM = 8;
  RCC_OscInitStruct.PLL.PLLN = 168;
  RCC_OscInitStruct.PLL.PLLP = RCC_PLLP_DIV2;
  RCC_OscInitStruct.PLL.PLLQ = 7;
  if (HAL_RCC_OscConfig(&RCC_OscInitStruct) != HAL_OK)
  {
    Error_Handler();
  }

  /** Initializes the CPU, AHB and APB buses clocks
  */
  RCC_ClkInitStruct.ClockType = RCC_CLOCKTYPE_HCLK|RCC_CLOCKTYPE_SYSCLK
                              |RCC_CLOCKTYPE_PCLK1|RCC_CLOCKTYPE_PCLK2;
  RCC_ClkInitStruct.SYSCLKSource = RCC_SYSCLKSOURCE_PLLCLK;
  RCC_ClkInitStruct.AHBCLKDivider = RCC_SYSCLK_DIV1;
  RCC_ClkInitStruct.APB1CLKDivider = RCC_HCLK_DIV4;
  RCC_ClkInitStruct.APB2CLKDivider = RCC_HCLK_DIV2;

  if (HAL_RCC_ClockConfig(&RCC_ClkInitStruct, FLASH_LATENCY_5) != HAL_OK)
  {
    Error_Handler();
  }
}

/**
  * @brief I2C2 Initialization Function
  * @param None
  * @retval None
  */
static void MX_I2C2_Init(void)
{

  /* USER CODE BEGIN I2C2_Init 0 */

  /* USER CODE END I2C2_Init 0 */

  /* USER CODE BEGIN I2C2_Init 1 */

  /* USER CODE END I2C2_Init 1 */
  hi2c2.Instance = I2C2;
  hi2c2.Init.ClockSpeed = 100000;
  hi2c2.Init.DutyCycle = I2C_DUTYCYCLE_2;
  hi2c2.Init.OwnAddress1 = 0;
  hi2c2.Init.AddressingMode = I2C_ADDRESSINGMODE_7BIT;
  hi2c2.Init.DualAddressMode = I2C_DUALADDRESS_DISABLE;
  hi2c2.Init.OwnAddress2 = 0;
  hi2c2.Init.GeneralCallMode = I2C_GENERALCALL_DISABLE;
  hi2c2.Init.NoStretchMode = I2C_NOSTRETCH_DISABLE;
  if (HAL_I2C_Init(&hi2c2) != HAL_OK)
  {
    Error_Handler();
  }
  /* USER CODE BEGIN I2C2_Init 2 */

  /* USER CODE END I2C2_Init 2 */

}

/**
  * @brief SPI1 Initialization Function
  * @param None
  * @retval None
  */
static void MX_SPI1_Init(void)
{

  /* USER CODE BEGIN SPI1_Init 0 */

  /* USER CODE END SPI1_Init 0 */

  /* USER CODE BEGIN SPI1_Init 1 */

  /* USER CODE END SPI1_Init 1 */
  /* SPI1 parameter configuration*/
  hspi1.Instance = SPI1;
  hspi1.Init.Mode = SPI_MODE_MASTER;
  hspi1.Init.Direction = SPI_DIRECTION_2LINES;
  hspi1.Init.DataSize = SPI_DATASIZE_8BIT;
  hspi1.Init.CLKPolarity = SPI_POLARITY_LOW;
  hspi1.Init.CLKPhase = SPI_PHASE_1EDGE;
  hspi1.Init.NSS = SPI_NSS_SOFT;
  hspi1.Init.BaudRatePrescaler = SPI_BAUDRATEPRESCALER_256;
  hspi1.Init.FirstBit = SPI_FIRSTBIT_MSB;
  hspi1.Init.TIMode = SPI_TIMODE_DISABLE;
  hspi1.Init.CRCCalculation = SPI_CRCCALCULATION_DISABLE;
  hspi1.Init.CRCPolynomial = 10;
  if (HAL_SPI_Init(&hspi1) != HAL_OK)
  {
    Error_Handler();
  }
  /* USER CODE BEGIN SPI1_Init 2 */

  /* USER CODE END SPI1_Init 2 */

}

/**
  * @brief SPI3 Initialization Function
  * @param None
  * @retval None
  */
static void MX_SPI3_Init(void)
{

  /* USER CODE BEGIN SPI3_Init 0 */

  /* USER CODE END SPI3_Init 0 */

  /* USER CODE BEGIN SPI3_Init 1 */

  /* USER CODE END SPI3_Init 1 */
  /* SPI3 parameter configuration*/
  hspi3.Instance = SPI3;
  hspi3.Init.Mode = SPI_MODE_MASTER;
  hspi3.Init.Direction = SPI_DIRECTION_2LINES;
  hspi3.Init.DataSize = SPI_DATASIZE_8BIT;
  hspi3.Init.CLKPolarity = SPI_POLARITY_LOW;
  hspi3.Init.CLKPhase = SPI_PHASE_1EDGE;
  hspi3.Init.NSS = SPI_NSS_SOFT;
  hspi3.Init.BaudRatePrescaler = SPI_BAUDRATEPRESCALER_128;
  hspi3.Init.FirstBit = SPI_FIRSTBIT_MSB;
  hspi3.Init.TIMode = SPI_TIMODE_DISABLE;
  hspi3.Init.CRCCalculation = SPI_CRCCALCULATION_DISABLE;
  hspi3.Init.CRCPolynomial = 10;
  if (HAL_SPI_Init(&hspi3) != HAL_OK)
  {
    Error_Handler();
  }
  /* USER CODE BEGIN SPI3_Init 2 */

  /* USER CODE END SPI3_Init 2 */

}

/**
  * @brief TIM1 Initialization Function
  * @param None
  * @retval None
  */
static void MX_TIM1_Init(void)
{

  /* USER CODE BEGIN TIM1_Init 0 */

  /* USER CODE END TIM1_Init 0 */

  TIM_ClockConfigTypeDef sClockSourceConfig = {0};
  TIM_MasterConfigTypeDef sMasterConfig = {0};

  /* USER CODE BEGIN TIM1_Init 1 */

  /* USER CODE END TIM1_Init 1 */
  htim1.Instance = TIM1;
  htim1.Init.Prescaler = 167;
  htim1.Init.CounterMode = TIM_COUNTERMODE_UP;
  htim1.Init.Period = 65535;
  htim1.Init.ClockDivision = TIM_CLOCKDIVISION_DIV1;
  htim1.Init.RepetitionCounter = 0;
  htim1.Init.AutoReloadPreload = TIM_AUTORELOAD_PRELOAD_DISABLE;
  if (HAL_TIM_Base_Init(&htim1) != HAL_OK)
  {
    Error_Handler();
  }
  sClockSourceConfig.ClockSource = TIM_CLOCKSOURCE_INTERNAL;
  if (HAL_TIM_ConfigClockSource(&htim1, &sClockSourceConfig) != HAL_OK)
  {
    Error_Handler();
  }
  sMasterConfig.MasterOutputTrigger = TIM_TRGO_RESET;
  sMasterConfig.MasterSlaveMode = TIM_MASTERSLAVEMODE_DISABLE;
  if (HAL_TIMEx_MasterConfigSynchronization(&htim1, &sMasterConfig) != HAL_OK)
  {
    Error_Handler();
  }
  /* USER CODE BEGIN TIM1_Init 2 */

  /* USER CODE END TIM1_Init 2 */

}

/**
  * @brief TIM2 Initialization Function
  * @param None
  * @retval None
  */
static void MX_TIM2_Init(void)
{

  /* USER CODE BEGIN TIM2_Init 0 */

  /* USER CODE END TIM2_Init 0 */

  TIM_ClockConfigTypeDef sClockSourceConfig = {0};
  TIM_MasterConfigTypeDef sMasterConfig = {0};

  /* USER CODE BEGIN TIM2_Init 1 */

  /* USER CODE END TIM2_Init 1 */
  htim2.Instance = TIM2;
  htim2.Init.Prescaler = 71;
  htim2.Init.CounterMode = TIM_COUNTERMODE_UP;
  htim2.Init.Period = 65535;
  htim2.Init.ClockDivision = TIM_CLOCKDIVISION_DIV1;
  htim2.Init.AutoReloadPreload = TIM_AUTORELOAD_PRELOAD_DISABLE;
  if (HAL_TIM_Base_Init(&htim2) != HAL_OK)
  {
    Error_Handler();
  }
  sClockSourceConfig.ClockSource = TIM_CLOCKSOURCE_INTERNAL;
  if (HAL_TIM_ConfigClockSource(&htim2, &sClockSourceConfig) != HAL_OK)
  {
    Error_Handler();
  }
  sMasterConfig.MasterOutputTrigger = TIM_TRGO_RESET;
  sMasterConfig.MasterSlaveMode = TIM_MASTERSLAVEMODE_DISABLE;
  if (HAL_TIMEx_MasterConfigSynchronization(&htim2, &sMasterConfig) != HAL_OK)
  {
    Error_Handler();
  }
  /* USER CODE BEGIN TIM2_Init 2 */

  /* USER CODE END TIM2_Init 2 */

}
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

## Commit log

2025-10-24 Deadline update (minimal set, Experiments excluded)
    [0.4 nozzle.0001.ipt, 0.4 nozzle.ipt, 1 X Left_Idler_Mount.0001.ipt, 1 X Left_Idler_Mount.ipt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]
2025-10-24 phase 2
    [PrintTask_2a.csv, PrintTask_2b.csv]
2025-10-24 some more trials
    [PrintTask_3.csv, PrintTask_4.csv]
2025-10-24 the rest of the experimental results
    [PrintTask_1.csv, PrintTask_5.csv, PrintTask_6.csv]
2025-11-03 Demo Preparation
    [FinalExtruder - Copy.0030.iam, FinalExtruder - Exploded view.iam, PrintTask.csv, Syringe Assembly - Exploded view.idw]
2025-11-04 Further demo prep
    [PrintTask.csv]
2025-11-11 2 days
    [PrintTask.csv]
2025-11-11 Add demo assets (PPTX, images, task generator, small videos)
    [PrintTask.csv]
2026-06-01 Temperature feedback updates
    [A4988 STEPPER MOTOR DRIVER CARRIER--3DModel-STEP-56544.ipt, BottomCase.0005.ipt, BottomCase.ipt, BottomCase.stl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]
